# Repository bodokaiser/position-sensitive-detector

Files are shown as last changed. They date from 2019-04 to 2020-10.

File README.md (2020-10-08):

# Position-sensitive detector

Position-sensitive detector using the Hamamatsu S5991-01 position-sensitive photodiode.

| Parameter | Value |
| --------- | ----- |
| Spatial resolution | 2 um |
| Bandwidth | 1400 kHz |
| Input voltage | +- 15 V |
| Output voltage | +- 12 V |

detector

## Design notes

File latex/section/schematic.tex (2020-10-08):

\section{Schematic}

The present section discusses the critical sections of the electrical schematics and should be consulted for reference if parameters, for example, bandwidth or gain, need to be adjusted.

\subsection{Photodiode frontend}

The photodiode frontend is responsible for converting the photocurrent to a voltage.
The most simple frontend, a resistor, has limited bandwidth.
Using a transimpedance amplifier, we can decouple the output voltage from the voltage swing across the diode.
The bandwidth is now limited by the amplifier gain.

\begin{figure}[H]
	\centering
	\includestandalone[mode=buildnew]{figure/circuit/amplifier-transimpedance-input-capacitance}
 	\caption{Transimpedance amplifier for photodiode}\label{fig:transimpedance_amplifier}
\end{figure}

\Cref{fig:transimpedance_amplifier} shows a transimpedance amplifier frontend circuit representing the photodiode by a current source with capacitance.
The current source relates to the power of the incident light by
\begin{equation}
I_\text{in} = S(\lambda) P,
\end{equation}
wherein $S(\lambda)$ is the spectral responsivity, also known as photosensitivity, and $P$ is the power of the light beam.

A class 2 laser can be operated without safety googles.
For a Class 2 laser, the beam power is limited to $P\leq\SI{1}{\milli\watt}$. With $S=\SI{0.6}{\ampere\per\watt}$, the photocurrent is limited to $I_\text{in}\leq\SI{0.6}{\milli\ampere}$.

The operational amplifier's output voltage in the transimpedance configuration is equal to
\begin{equation}
	V_\text{out} = - R_f I_\text{in}.
	\label{eq:transimpedance_amplifier_output_voltage}
\end{equation}
The operational amplifier's output voltage is determined by it's supply voltages.
For a rail-to-rail operational amplifier it is equal to the supply voltage.
For example, if the supply voltage is \SI{\pm5}{\volt}, \cref{eq:transimpedance_amplifier_output_voltage} gives us a value for the feedback resistance,
\begin{equation}
	R_f\geq\abs{\frac{V_\text{out}}{I_\text{in}}}=\abs{\frac{V_\text{supply}}{I_\text{in}}}
	\label{eq:feedback_resistance}.
\end{equation}
Using the previous estimated photocurrent of a class 2 laser, $I_\text{in}=\SI{0.6}{\milli\ampere}$, $V_\text{supply}=\SI{\pm5}{\volt}$, and \cref{eq:feedback_resistance}, we find that $R_f\approx\SI{9}{\kilo\ohm}$ would make our transimpedance amplifier saturate at the maximal expected light power.

A feedback capacitance
\begin{equation}
	C_f\geq\sqrt{\frac{C_\text{in}}{2\pi R_f f_u}},
	\label{eq:feedback_capacitance}
\end{equation}
wherein $f_u$ is the \gls{gbp} of the operational amplifier,
 is sufficient for stability.
 In general, the input capacitance of the operational amplifier adds to the input capacitance.
 In practice, solder joints and \gls{pcb} traces may add to the capacitance such that a slightly higher value than given by \cref{eq:feedback_capacitance} is recommended.
 However, if the feedback capacitance is too high, we remove high-frequency components of our signal, which might be of interest.
 
The photodiode's datasheet specifies the capacitance $C_\text{in}$ to be about \SI{90}{\pico\farad} if reverse-biased at \SI{10}{\volt}.
The differential- and common-mode input capacitance of the OPA847 operational amplifier add up to a total input capacitance of \SI{98}{\pico\farad}.
Using $R_f=\SI{10}{\kilo\ohm}$ and \gls{gbp} of $f_u=\SI{10}{\mega\hertz}$, a feedback capacitance of at least $C_f=\SI{12.5}{\pico\farad}$ should be choosen.

\subsection{Voltage regulator}

We use two voltage regulators to maintain a constant voltage of \SI{\pm12}{\volt} from the external \SI{\pm15}{\volt} power supply. The \SI{\pm12}{\volt} voltage powers most components except the transimpedance amplifiers of the detector.
Using a dedicated pair of voltage regulators to power the transimpedance amplifiers decreases the load on the primary voltage regulator.

\Cref{fig:voltage_regulator} shows the circuitry of the primary voltage regulators that output \SI{\pm12}{\volt}.
The positive voltage regulator U1 of type LM317 and the negative voltage regulator U2 of type LM337 have an internal reference voltage of \SI{1.25}{\volt}.

\begin{figure}[H]
	\centering
	\includestandalone[mode=buildnew]{figure/circuit/voltage-regulator}
	\caption{Dual supply voltage regulator}\label{fig:voltage_regulator}
\end{figure}

The voltage divider comprising R1 and R2 fixes the output voltage according to
\begin{equation}
	V_\text{out}=\SI{1.25}{\volt}\left(1+\frac{R_2}{R_1}\right).
\end{equation}
With $R1 = \SI{240}{\ohm}$ and $R2 = \SI{2.2}{\kilo\ohm}$, the output voltage is about \SI{12.7}{\volt}, which leaves enough space for potential voltage drops in, for example, the operational amplifiers.

Diodes D1 and D3 ensure that the capacitors C3 and C5 can discharge over the external power supply.

The application notes of one of the voltage regulator's datasheets describe the presented design.
That is also the reason for not using fixed voltage regulators in this case.

\subsection{Voltage reference}

Reverse biasing the photodiode decreases it's capacitance and thereby increases the bandwidth.
The reverse bias voltage needs to be well controlled not to cause any side-effects.
Therefore, we utilize a voltage reference to supply a highly-regulated reverse voltage for the photodiode.

\begin{figure}[H]
	\centering
	\includestandalone[mode=buildnew]{figure/circuit/voltage-reference}
	\caption{Voltage reference to reverse bias the photodiode}\label{fig:voltage_reference}
\end{figure}

\Cref{fig:voltage_reference} shows the schematic of the reverse-bias voltage reference.
The capacitors C1 and C3 intercept voltage fluctuations. 
Resistor R1 forms a low-pass with capacitor C2 that suppresses frequencies above 160 Hz.

\subsection{Analog arithmetic}

Finally, we need to add and subtract the four different voltage signals of the position-sensitive photodiode to obtain quantities proportional to the incident light beam's center-of-mass.
We achieve immutability of the input signals for addition and subtraction with the summing amplifier.
We extend the summing amplifier to allow negative signs, i.e., subtraction.

\begin{figure}[H]
	\centering
	\includestandalone[mode=buildnew]{figure/circuit/amplifier-arithmetic}
	\caption{Summing and difference amplifier}\label{fig:amplifier_arithmetic}
\end{figure}

\Cref{fig:amplifier_arithmetic} shows such an arithmetic amplifier.
According to \cite[p. 5]{Tietze15} the output voltage is given by
\begin{equation}
	V_\text{out}=-\frac{R_1}{R_f}V_1-\frac{R_2}{R_f}V_2+\frac{R_3}{R_f}V_3+\frac{R_4}{R_f}V_4.
	\label{eq:arithmetic_amplifier_output_voltage}
\end{equation}

It is an excellent directive to have a well-controlled bandwidth.
On this account, we include capacitor $C_f$ to control the frequency response of the amplifier. 
For the resistor and capacitor configuration used in \cref{fig:amplifier_arithmetic}, the bandwidth is equal to
\begin{equation}
	\frac{1}{2\pi R_fC_f}\approx\SI{3}{\mega\hertz},
\end{equation}
magnitudes more than the bandwidth of our transimpedance amplifiers.
We place an additional capacitor with feedback capacitance at the non-inverting input of the operational amplifier to obtain a symmetric frequency response for the positive terms in \cref{eq:arithmetic_amplifier_output_voltage}.

The value of the resistors is \SI{10}{\kilo\ohm} to limit the current flow.

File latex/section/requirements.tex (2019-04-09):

\section{Requirements}

% TODO: precision and accuracy
% TODO: motivate bandwidth 1 kHz

The device should be powered by a dual voltage supply of \SI{15}{\volt} using a 4 pin LEMO connector.
The components on the printed circuit board should be assembled using surface-mount technology.
The device including casing should have a width below \SI{8}{\centi\meter} and a height below \SI{20}{\centi\meter}, preferably smaller, such that it can be integrated easily into existing optical setups.
The optical detector should be located as close to the bottom of the device as possible, as it allows greater height compatibility.

The spatial resolution of the center of mass of the incident light should be about \SI{1}{\micro\meter}.
Offset errors are tolerable as long as precision is high.
We aim for a signal bandwidth of \SI{10}{\kilo\hertz}.
The radiant flux of the incident light should be in the microwatt range.

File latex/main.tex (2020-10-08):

\documentclass[
	a4paper,
	parskip
]{scrartcl}

\usepackage[english]{babel}
\usepackage{authblk}
\usepackage{amsthm}
\usepackage{amsmath}
\usepackage{amssymb}
\usepackage{booktabs}
\usepackage{float}
\usepackage{multirow}
\usepackage{enumitem}
\usepackage{physics}
\usepackage{siunitx}
\usepackage{hyperref}
\usepackage{cleveref}
\usepackage{subcaption}
\usepackage{pgfplots}
\usepackage[backend=bibtex]{biblatex}
\usepackage{csquotes}
\usepackage[american]{circuitikz}
\usepackage{glossaries}
\usepackage[subpreambles=true]{standalone}

\makeglossaries
\newglossaryentry{s5990}{name=S5990, description={Hamamatsu two-dimensional PSD}}
\newacronym{ic}{IC}{integrated circuit}
\newacronym{ir}{IR}{infrared}
\newacronym{psd}{PSD}{position-sensitive detector}
\newacronym{gbp}{GBP}{gain-bandwidth-product}
\newacronym{pcb}{PCB}{printed circuit board}
\newacronym{bom}{BOM}{bill of materials}
\newacronym{smd}{SMD}{surface mounted device}
\newacronym{sma}{SMA}{SubMiniature version A}
\newacronym{bnc}{BNC}{Bayonet Neill–Concelman}
\newacronym{html}{HTML}{hypertext markup language}

\pgfplotsset{compat=1.17}

\graphicspath{{image/}}

\bibliography{literature.bib}

% https://tex.stackexchange.com/questions/247681/how-to-create-checkbox-todo-list/313337
\newlist{todolist}{itemize}{2}
\setlist[todolist]{label=$\square$}

\title{Position-sensitive detector}
\author{Bodo Kaiser}
\affil{Ludwig-Maximilians-Universität München}
\affil{\textit{bodo.kaiser@physik.uni-muenchen.de}}

\begin{document}

\maketitle
\tableofcontents

\include{section/introduction}
\include{section/position-sensitive-photodiode}
\include{section/operational-amplifier}
\include{section/schematic}
\include{section/production}
\include{section/measurement}

\appendix
\include{appendix/troubleshooting}

\printglossaries
\printbibliography

\end{document}

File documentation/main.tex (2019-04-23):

\documentclass[
	a4paper,
	parskip
]{scrartcl}

\usepackage[english]{babel}
\usepackage{authblk}
\usepackage{amsthm}
\usepackage{amsmath}
\usepackage{amssymb}
\usepackage{booktabs}
\usepackage{float}
\usepackage{multirow}
\usepackage{physics}
\usepackage{siunitx}
\usepackage{hyperref}
\usepackage{cleveref}
\usepackage{subcaption}
\usepackage{pgfplots}
\usepackage[
  backend=biber,
  sorting=none
]{biblatex}
\usepackage[american]{circuitikz}
\usepackage{glossaries}

\addbibresource{literature.bib}

\makeglossaries
\newglossaryentry{s5990}{name=S5990, description={Hamamatsu two-dimensional PSD}}
\newacronym{psd}{PSD}{position-sensitive detector}
\newacronym{gbp}{GBP}{gain-bandwidth-product}

\title{Position-sensitive device}
\author{Bodo Kaiser}
\affil{Ludwig-Maximilians-Universität München}
\affil{\textit{bodo.kaiser@physik.uni-muenchen.de}}

\begin{document}

\maketitle
\tableofcontents

\include{section/introduction}
\include{section/requirements}
\include{section/detector}
\include{section/preamplifier}
\include{section/power}

% TODO: signal processing of non-linear response Cui10
% TODO: mention current analog-to-digital-converter in a digital signal processing section

% TODO: bill of materials / component and package selection section
% TODO: pcb design section
% TODO: manufacturing section
% TODO: section for electrical and optical test setups to check functionality

\printglossaries
\printbibliography

\end{document}

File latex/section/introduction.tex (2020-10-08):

\section{Introduction}

We define a position-sensitive device as a device that outputs voltages proportional to the center of mass coordinates of a light beam incident on a sensitive area.

The present document summarizes the insights acquired on the journey of building such a device.

\subsection{Motivation}

Position-sensitive devices are used in a wide range of industrial and commercial applications, including displacement sensing and beam alignment, see Ref.~\cite[p.~22]{Maekynen00}.

We are interested in using a position-sensitive device for beam pointing alignment in our quantum optics laboratory.

The beam pointing refers to a laser beam's spatial focus and can change through thermal and mechanical effects.
Uncompensated changes in beam alignment can quickly degrade the overall performance of an optical system.
Therefore, it is crucial to align the beam pointing to ensure the optical system's proper operation at hand.

\subsection{Overview}

This document is organized as follows.

The first two sections introduce the theory of the (position-sensitive) photodiode and the operational amplifier.
These sections are rather elaborate and should be skipped by the pragmatic scientist.

The third section describes the (electrical) schematics of the detector.
If you want to adjust parameters, e.g., gain or bandwidth, you should read these sections.

The fourth section is the only significant section if you want to build a \gls{psd}.
If you also want an example of using the \gls{psd} in an optical setup to determine the spatial resolution, you should also read the fifth section.
Finally, the appendix gives some guidance on troubleshooting.

\subsection{Requirements}

The requirements are specified rather loose. The only hard requirement concerns the connectors and voltages of the power supply. The power connector should be a LEMO4 whose pin configuration is compatible with the \SI{\pm15}{\volt} dual-voltage power supplies used in the labs. Features that would be nice to have are:
\begin{enumerate}
	\item The device should be sensible with optical powers that are safe to operate, i.e., $P<\SI{1}{\micro\watt}$. There is no preferred wavelength.
	\item For easy integration into existing optical setups, the device should be as compact as possible. Additional space, if needed, should be occupied by elonging the height. The sensitive area of the detector should be on the bottom. The connectors should be on the top to avoid cables blocking the beam path.
	\item It should be possible to mount different detector sizes on the device.
\end{enumerate}
The range of the output voltages of the device can be chosen for the optimal signal-to-noise ratio.

\subsection{Specification}

\begin{figure}[H]
	\centering
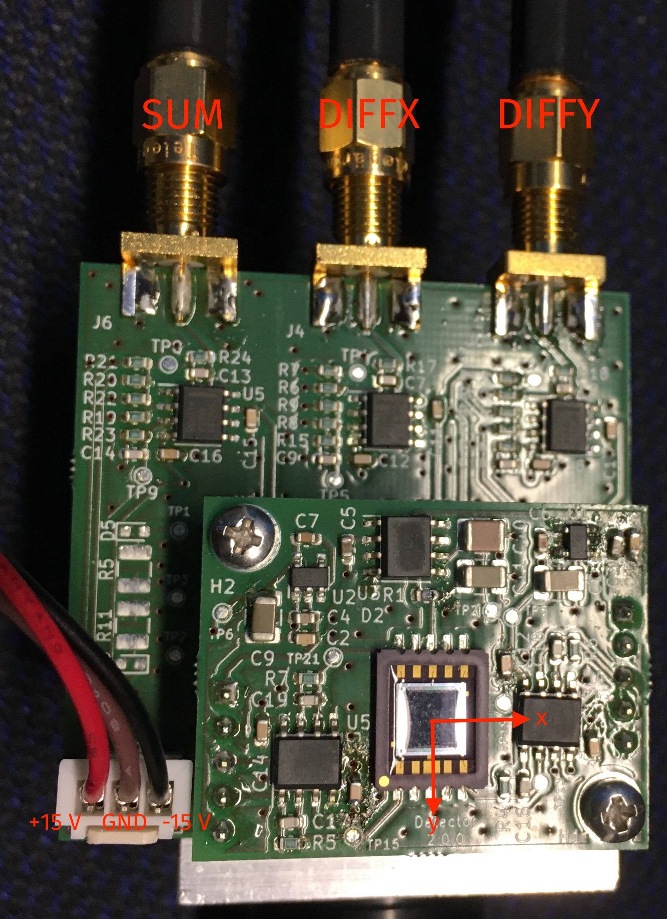
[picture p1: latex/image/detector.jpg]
	
	\caption{\gls{psd} on optical mount with connected cables}\label{fig:detector}
\end{figure}
\Cref{fig:detector} shows an image of the \gls{psd}.
The output voltage signals can be tapped from the upper \gls{sma} connectors.
The upper left connector gives the SUM voltage which reflects the total intensity of the optical signal.
The upper center connector gives the DIFFX voltage which reflects the difference proportional to the horizontal position on the sensitive area.
The upper right connector gives the DIFFY voltage which is proportional to the vertical position.
The SUM voltage is required to normalize the difference signals.
The DIFFX voltage increases when moving the light beam on the sensitive area to the right while the DIFFY voltage increases while moving the light beam to the bottom.
The device is powered by a 3-pin connector.
The outer (left) cable is the positive \SI{+15}{\volt} supply while the opposite cable is negative \SI{-15}{\volt} supply.
The center cable of the 3-pin connector has to reference ground.
The power connector has no polarity protection so be careful!

\begin{table}[htb]
  \centering
  \begin{tabular}{lcccc}
    \toprule
      Parameter & Minimum & Typical & Maximum \\
    \midrule
      Output voltages & \SI{-13}{\volt} & \SIrange{-2}{+2}{\volt} & \SI{+13}{\volt} \\
      Supply voltages & \SI{\pm13}{\volt} & \SI{\pm15}{\volt} & \SI{\pm37}{\volt} \\
      Spatial resolution & \SI{5.0}{\micro\meter} & \SI{2}{\micro\meter} & \SI{1}{\micro\meter} \\
      Bandwidth & & \SI{1400}{\kilo\hertz} & \\
    \bottomrule
  \end{tabular}
  \captionsetup{width=.8\textwidth}
  \caption{Specifications of the presented \gls{psd}}\label{tab:specifications}
\end{table}
\Cref{tab:specifications} summarizes the specifications of the presented \gls{psd}.
These specifications are only a rough estimate and we only assembled one \gls{psd} so far.

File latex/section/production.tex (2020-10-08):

\section{Production}

The production of the position-sensitive device involves the necessary steps to produce the detector and arithmetic \gls{pcb}.

It's best to first do the arithmetic board and if it works, proceed with the detector.
Of course, if you only need one of the boards, perform the following steps only once.

\subsection{Commissioning}

% TODO: screenshots of HTML BOM files

Before we can assemble the \gls{pcb}s, we need to gather the required components and order missing pieces.

The list of the required components is usually known as the \gls{bom}.
You can generate a current \gls{bom} directly from \href{https://kicad-pcb.org}{KiCad} by using the \href{https://github.com/openscopeproject/InteractiveHtmlBom}{InteractiveHtmlBom} plugin.
The plugin generates an \gls{html} file that lists the components and their respective placement on the \gls{pcb}.
\Cref{fig:kicad_interactive_html_bom_plugin_menu} shows where to find the plugin in the \gls{pcb} editor menu.
You can check if the parts are stocked and placed.
\begin{figure}[H]
	\centering
	
	\caption{Menu entry for the \href{https://github.com/openscopeproject/InteractiveHtmlBom}{InteraciveHtmlBom} plugin for \href{https://kicad-pcb.org}{KiCad}}\label{fig:kicad_interactive_html_bom_plugin_menu}
\end{figure}
\Cref{fig:kicad_interactive_html_bom_plugin_arithmetic} and \cref{fig:kicad_interactive_html_bom_plugin_detector} show the view of the generated \gls{html} for the arithmetic and detector board.
\begin{figure}[H]
	\centering
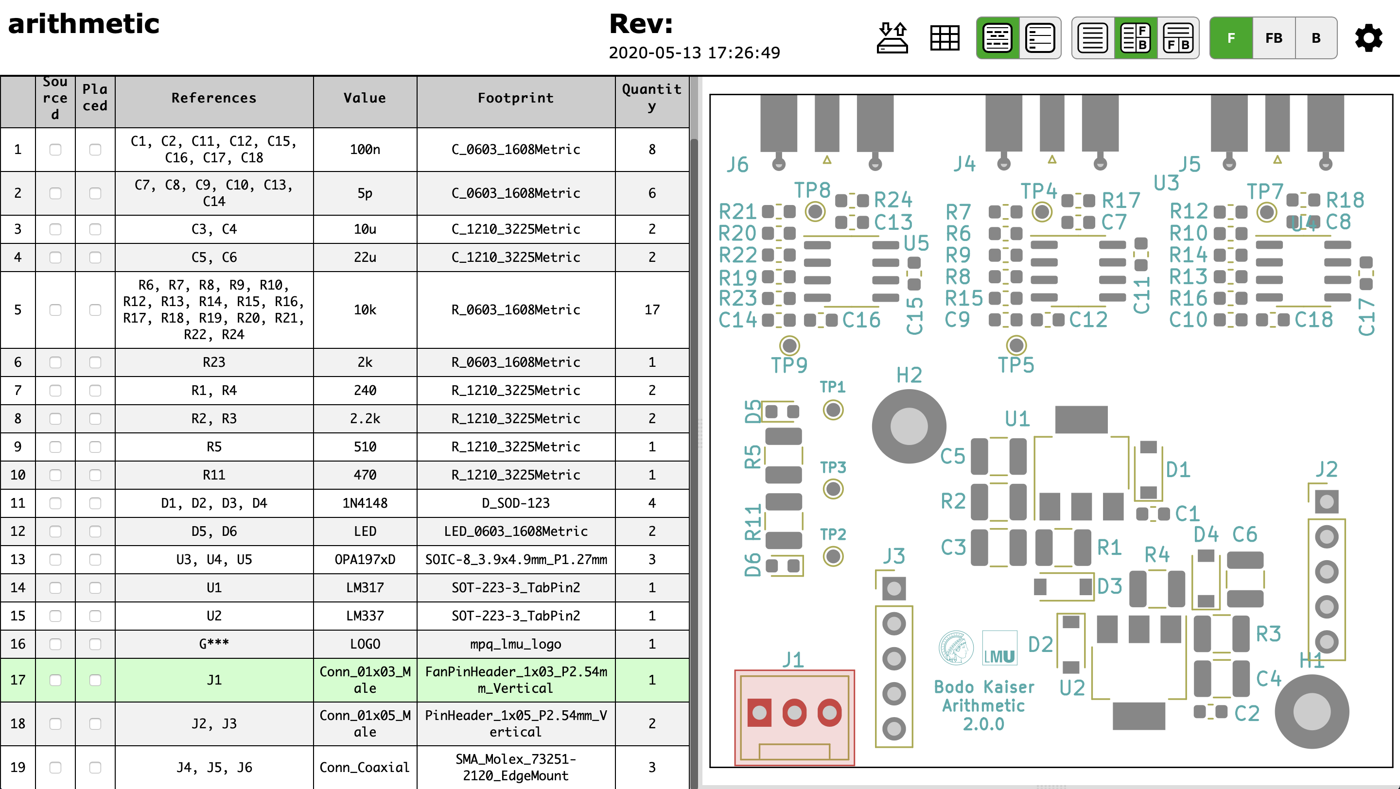
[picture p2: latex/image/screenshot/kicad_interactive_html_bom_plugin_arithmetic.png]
	
	\caption{Arithmetic board view of the \href{https://github.com/openscopeproject/InteractiveHtmlBom}{InteraciveHtmlBom} plugin}\label{fig:kicad_interactive_html_bom_plugin_arithmetic}
\end{figure}
\begin{figure}[H]
	\centering
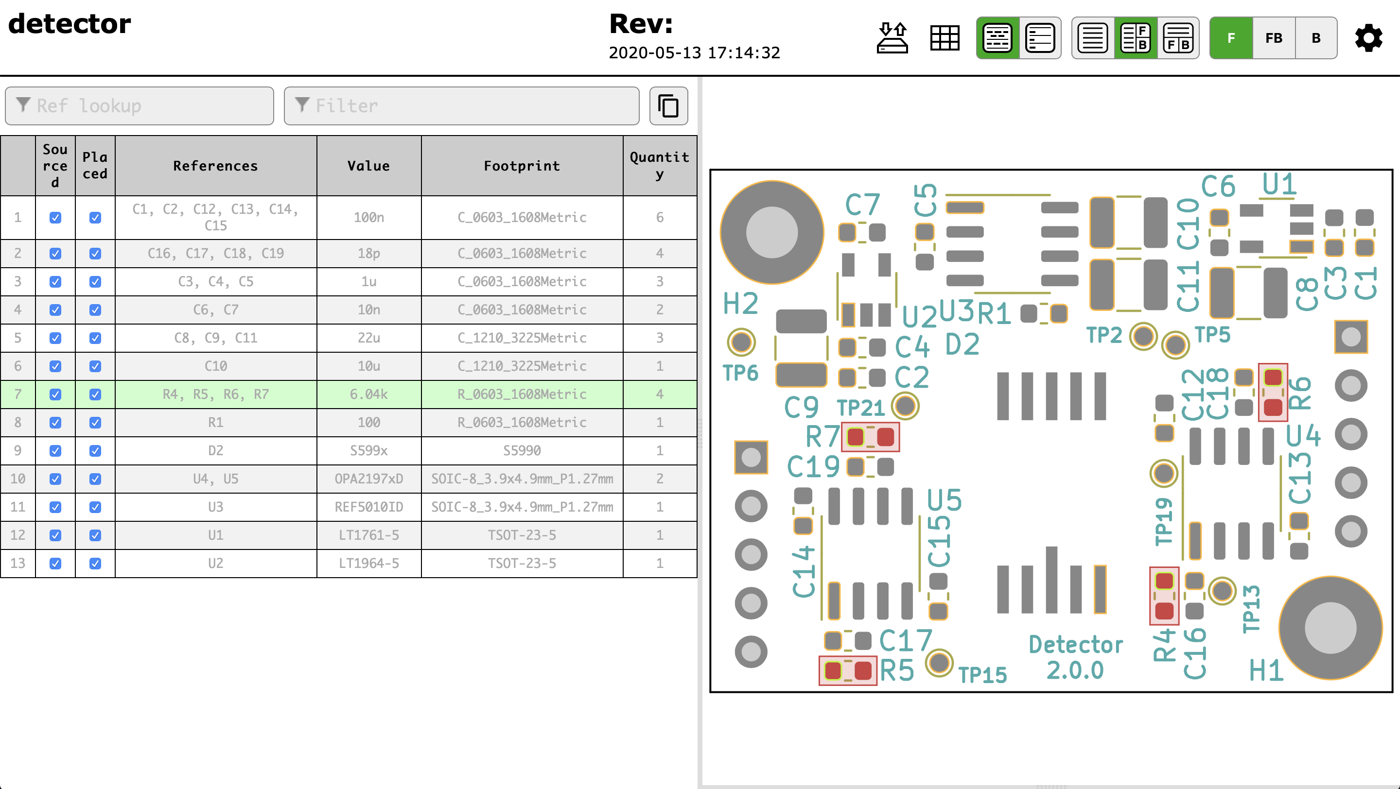
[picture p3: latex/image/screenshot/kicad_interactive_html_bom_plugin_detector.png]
	
	\caption{Detector board view of the \href{https://github.com/openscopeproject/InteractiveHtmlBom}{InteraciveHtmlBom} plugin}\label{fig:kicad_interactive_html_bom_plugin_detector}
\end{figure}
Start by checking the local inventory for the components listed by the generated \gls{html} \gls{bom}.
If certain elements are missing, you can check the \path{BOM.xlsx} file inside the project repository.
It contains part numbers and product links from major electronic distributors.
If you order, double-check with the generated \gls{html} \gls{bom}.
There might be errors, e.g., wrong casing sizes in the \path{BOM.xlsx} as it is potentially outdated.

\subsection{Manufacturing}

In the manufacturing process, we solder the components onto the PCB.
We recommend to proceed in the following steps:

\begin{enumerate}
    \item Put on rubber gloves as the solder paste is potentially hazardous.
    \item  Take out the solder paste from the fridge and let it reach room temperature\footnote{It is possible to use the cold solder paste directly, but it makes the handling more difficult as the paste is less fluid.}.
    \item Place the solder paste onto the contacts of the \gls{pcb}\footnote{Generally speaking, it is better to have too much solder paste then too less. If there is a small overlap between the contacts, this is fine as the solder will shrink when transitioning to a liquid phase in the oven.}.
    \item Place the \gls{smd} components onto the solder with a tweezer\footnote{Start with the larger components and then progress to the smaller ones}.
    \item Start the oven and adjust the frame on which you place the board with the screw to the appropriate size. Use an empty \gls{pcb} for this.
    \item Select the profile SMD180 and follow the instructions of the oven.
    \item Inspect the board for misplaced components and unmelted solder, and fix them by hand soldering\footnote{You can use the solder heat gun to melt the remaining solder paste or remove misplaced components. 
However, you might blow away small capacitors.}.
	\item Perform electrical testing as described in the next section.
	\item Solder remaining components, for example, the \gls{sma} mounts or the pin headers, by hand.
\end{enumerate}

\subsection{Electrical testing}

With the electrical testing, we want to confirm that the solder connections and components work as expected.
The most basic check is that the supply voltages are correct.
More elaborated checks concern the operational amplifiers but are out of the scope of this document.

For the arithmetic perform the following checks in the given order.
Skipping steps might lead to permanent damage!
\begin{todolist}
	\item Leave the arithmetic board unpowered and check for high resistance between the supply lines through the test points TP1 (\SI{+12}{\volt}), TP2 (GND), and TP3 (\SI{-12}{\volt})\footnote{If there is low resistance ($>\SI{10}{\kilo\ohm}$), you probably have a short through soldering.}.
	\item Configure the power supply to provide a dual voltage of \SI{\pm15}{\volt}\footnote{Alternatively, use two single voltage sources set to \SI{15}{\volt} and connect the negative port of one of the voltage sources with the other one's positive voltage.}. If possible, limit the current of the voltage sources.
	\item Confirm that the output voltages are correct with the multimeter.
	\item Connect the power supply with the arithmetic board but double-check the polarity.
	\item The voltage between TP2 and TP1 should read around \SI{+12}{\volt} while the voltage between TP2 and TP3 should read about \SI{-12}{\volt}.
	\item Confirm that the supply voltages reach the op-amps.
	\item Check the temperature of the \gls{ic}s. If any \gls{ic} is very hot, there is a short.
	\item Check if the op-amps' output voltage changes by grounding the inverting input.
\end{todolist}

For the detector perform the following checks in the given order.
Skipping steps might lead to permanent damage!
\begin{todolist}
	\item Leave the detector board unplugged and confirm high resistance between GND (you can use the middle pin of the headers), TP5 (\SI{+5}{\volt}), and TP6 (\SI{-5}{\volt}).
	\item Confirm a change of the voltage between the photodiode and GND's outer pins while illuminating the sensitive area of the photodiode with a laser pointer.
	\item Mount the detector board on the arithmetic board, and measure the detector board's supply voltages.
	\item Confirm that the voltage reference (U3) outputs \SI{10}{\volt} and that the op-amps have the correct supply voltage of \SI{\pm5}{\volt}.
\end{todolist}

Finally, we test the arithmetic amplifiers on the arithmetic board.
\begin{todolist}
	\item Mount the detector onto the arithmetic board.
	\item Measure the voltage at the outputs of the operational amplifiers of the arithmetic board. For the summing amplifier (U5), we expect an increase in voltage when illuminating the photodiode with the laser pointer.
For the difference amplifiers (U3, U4), we expect the voltage to change when moving the laser pointer's focal spot on the photodiode.
\end{todolist}

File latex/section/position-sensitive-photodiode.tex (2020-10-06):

\section{Position-sensitive photodiode}

The present section gives an introduction to the semiconductor theory for a position-sensitive photodiode.
We start from the description of a p-n junction and extend the description to the position-sensitive photodiode.
After that, we discuss the evolution of position-sensitive photodiode designs.
Finally, we derive an analytical relation between the photocurrents and the light focus's position on the sensitive area.

\subsection{Transverse photodiodes}

The purpose of the following section is to recall the mechanics of the (transverse) photoeffect observed in an illuminated p-n junction.
Figures and the description thereof are primarily based on Ref.~\cite{Simon13}.
A subtle difference in the depicted figures and the figures of Ref.~\cite{Simon13} is that we exchanged the order of p- and n-type semiconductors.
We found this order to be more intuitive when referring to a p-n junction.
\begin{figure}[H]
	\centering
	\includestandalone[mode=buildnew]{figure/diagram/pn-junction-separated}
	\caption{Separated p- and n-type semiconductor with holes (white) and electrons (black).}\label{fig:pn_junction_separated}
\end{figure}
\Cref{fig:pn_junction_separated} shows a separated p- and n-type semiconductor.
We see an illustration of the p- and n-type semiconductors with their respective mobile charge carriers in the upper half.
The p-type semiconductor has an excess of positive charge carriers (holes), depicted as white circles.
The n-type semiconductor has an excess of negative charge carriers (electrons), depicted as black circles.
The excess charge carriers form due to the implantation of acceptor and donator ions and are indicated as circles with plus and minus sign in \Cref{fig:pn_junction_separated}.
The implanted ions have more or fewer electrons than the atoms of the semiconductor material.
Therefore donating an electron or accepting an electron and effectively forming a hole as an absence of negative charge.
The lower half of \Cref{fig:pn_junction_separated} shows the energy band structure of both p- and n-type semiconductors.
The lower energy band represents the valence band made up of the tightly bound electrons.
The upper energy band represents the conduction band made up of electrons that are are not bound to a single atomic core but shared across the lattice.
Charge carriers in the conduction band can move freely and thereby contribute to the conductivity of the material.
For an undoped (intrinsic) semiconductor, the chemical potential is in the center of the bandgap between the conduction and valence band.
Doping shifts the chemical potential in the p- and n-type semiconductors.
In the p-type semiconductor, acceptor ions can take up electrons from the conduction band, thereby decreasing the chemical potential.
In the n-type semiconductor, donator ions contribute electrons to the conduction band, increasing the chemical potential.
\begin{figure}[H]
	\centering
	\includestandalone[mode=buildnew]{figure/diagram/pn-junction-combined}
	\caption{Combined p- and n-type semiconductor with holes (white) and electrons (black).}\label{fig:pn_junction_combined}
\end{figure}
In \Cref{fig:pn_junction_combined} the p- and n-type semiconductors are brought into contact with each other, forming a p-n junction.
Close to the junction, holes and electrons recombine due to a diffusion process, leaving an electrically charged area.
The electrically charged area creates an electrostatic potential across the junction, as illustrated in the lower part of \Cref{fig:pn_junction_combined}.
We refer to this area as the depletion region.
In \Cref{fig:pn_junction_combined} the depletion region expands between the dashed lines around the junction.
\begin{figure}[H]
	\centering
	\includestandalone[mode=buildnew]{figure/diagram/pn-junction-energy}
	\caption{Energy bands of the p-n junction.}\label{fig:pn_junction}
\end{figure}
The energy band diagram in \Cref{fig:pn_junction} accounts for the shift in energy due to the electrostatic potential.
The chemical potentials of both sides of the junction are now aligned.
The energy required to excite an electron on the p-type side from the valence to the conduction band and the energy needed to excite a hole from the conduction to the valence band are equal to the bandgap of the semiconductor.
Suppose one applies a reverse bias voltage across the p-n junction. In that case, the effective energy gap between conduction and valence band is reduced, the electrostatic potential increases, and the depletion region broadens.
\Cref{fig:pn_junction_reverse} depicts the situation of an applied reverse voltage.
\begin{figure}[H]
	\centering
	\includestandalone[mode=buildnew]{figure/diagram/pn-junction-energy-reverse}
	\caption{Energy band diagram of a reverse biased p-n junction.}\label{fig:pn_junction_reverse}
\end{figure}
The current-voltage characteristic of the p-n junction is described by the Schockley diode equation,
\begin{equation}
	I_\text{diode}=I_\text{sat}(T)\left(e^{eV/k_BT}-1\right)
	\label{eq:diode_current},
\end{equation}
wherein $I_\text{sat}\propto e^{-E_\text{gap}/k_BT}$ is the temperature dependent reverse bias saturation current and $V$ the voltage applied to the p-n junction.
Using the proportionality of the reverse bias saturation current, we can write,
\begin{equation}
	I_\text{diode}\propto e^{\left(eV-E_\text{gap}\right)/k_BT}-e^{-E_\text{gap}/k_BT}\label{eq:diode_current_prop},
\end{equation} 
which discloses the two effects contributing to the diode current.
The left-hand side of the proportionality of \Cref{eq:diode_current_prop} represents the current contribution due to intra-band excitation of charge carriers, whereas the right-hand side represents the current contribution due to inter-band excitation.
\begin{figure}[H]
	\centering
	\includestandalone[mode=buildnew]{figure/plot/diode-current-voltage}
	\caption{Current-voltage characteristics of a p-n junction with different levels of illumination.}\label{fig:pn_junction_iv}
\end{figure}
In \Cref{fig:pn_junction_iv} we see the current-voltage characteristics of the p-n junction under different levels of illumination.
For negative voltages, the p-n junction is operated under reverse bias.
If the reverse bias voltage exceeds the breakdown voltage, the p-n junction starts to conduct.
The reverse saturation current is the amount of current necessary for the breakdown. The curve shifts downwards with increasing illumination.
The separation between the non-illuminated (top curve) and illuminated curves represent the respective photocurrent.

The conversion rate of photons to photoelectrons depends on the type of the bandgap, i.e., direct or indirect, the wavelength $\lambda$ of the photon, and the temperature $T$.
Most photodiodes report a wavelength $\lambda$ dependent responsitivity $R$ which can be used to convert the radiant flux $P$ of the incident light to the generated photocurrent $I_\text{photo}$,
\begin{equation}
	I_\text{photo}=R(\lambda)P
	\label{eq:responsitivity}.
\end{equation}
For silicon-based p-n junctions, the responsitivity $R(\lambda)$ is between \SI{0.2}{\ampere\per\watt} at \SI{400}{\nano\meter} and \SI{0.6}{\ampere\per\watt} at \SI{950}{\nano\meter}.

\begin{figure}[H]
	\centering
	\includestandalone[mode=buildnew]{figure/diagram/pn-junction-energy-illumination}
	\caption{Energy diagram of a reverse biased p-n junction under illumination.}\label{fig:pn_junction_illumination}
\end{figure}
\Cref{fig:pn_junction_illumination} shows a p-n junction under reverse bias where a photon excites an electron-hole pair in the depletion region.
Due to the electrostatic potential, the electrons are accelerated to the right. Analogue, the holes are accelerated to the left. The photocurrent, a diode current, \Cref{eq:diode_current}, flows across the junction.

\subsection{Lateral photodiodes}

In the previous section, we discussed the transversal photoeffect associated with the p-n junction's illumination.
In addition to the transversal photoeffect, the lateral photoeffect was first discovered by W. Schottky~\cite{Schottky30} in 1930 and later rediscovered in 1957 by J. Wallmark~\cite{Wallmark57}.
In the present section, we summarize key results from Ref.~\cite{Noorlag74}, and Ref.~\cite{Woltring75}. The focus of our summary is on the most common position-sensitive photodiode design, the tetralateral photodiode.
\begin{figure}[H]
	\centering
	\includestandalone[mode=buildnew]{figure/diagram/pn-junction-lateral-cross-section}
	\caption{Cross section of a lateral photodiode.}\label{fig:lateral_photodiode_cross_section}
\end{figure}
\Cref{fig:lateral_photodiode_cross_section} depicts the cross-section of a lateral photodiode with a p-type semiconductor as the top, an n-type semiconductor as the middle layer, and a resistive material as the bottom layer.
The photodiode's common cathode is an electric contact into the top layer.
One can ground or apply a positive voltage to the common cathode. If we apply a positive voltage, we say that the photodiode is reverse-biased.
In contrast to the transversal photodiode, the lateral photodiode has two anode contacts positioned at the opposite sites embedded into the resistive layer.
An almost linear relation between the photocurrent at each of the anode contacts and the incident light spot's center-of-mass exists.
Therefore the lateral photodiode can be used to measure the spatial coordinate of an incident light spot.

The dynamics of the lateral photodiode are guided by the Lucovsky~\cite{Lucovsky60} equation,
\begin{equation}
	\nabla^2V=\frac{\rho}{w}J_s\left(e^{eV/k_BT}-1\right)-\frac{\rho_d}{w}J_p\label{eq:lucovsky_exact},
\end{equation}
wherein $V$ is the diode voltage, $\rho$ is the resistance per unit length of the resistive layer, $J_s$ is the reverse-bias saturation current and $J_p$ is the photocurrent generated due photon induced electron-hole excitation.
\Cref{eq:lucovsky_exact} can be obtained by a combination of the current density continuity equation with Ohm's law and the Schottky equation, \Cref{eq:diode_current}.

According to Ref.~\cite{Woltring75}, operation of the lateral in fully reverse-bias has the following benefits:
\begin{enumerate}
	\item Reduced signal loss.
	\item Improved response speed and resolution.
	\item Improved linearity of the position.
	\item Reduced temperature dependence.
\end{enumerate}
In electronic engineering literature, e.g., Ref.~\cite[p.~258]{Jung05}, one is sometimes discouraged from operating a photodiode under reverse-bias for the highest sensitivity as the reverse-bias increased the diode leakage (dark) current.
We believe that as long as the dark current is significantly smaller than the typical photocurrent, the photodiode should always be operated in the reverse-bias mode as recommended by Ref.~\cite{Noorlag74,Woltring75,Wang89,Hobbs11}.

Assuming a fully reverse-biased lateral photodiode, we have $eV/k_BT\ll1$ and \Cref{eq:lucovsky_exact} simplifies to a linear second order differential (Poisson) equation,
\begin{equation}
	\nabla^2V\approx-\frac{\rho}{w}\left(J_s+J_p\right)
	\label{eq:lucovsky_reverse_bias},
\end{equation}
which can be solved using variable separation and a product Ansatz.
The solution of \Cref{eq:lucovsky_reverse_bias} depends on the imposed boundary conditions.
The Dirichlet boundary condition, $V=0$, should be used if an electrical contact terminates the semiconductor. Otherwise, the Neumann boundary condition, $\pdv{V}{n}=0$, should be assumed.
\begin{figure}[H]
	\centering
	\includestandalone[mode=buildnew]{figure/diagram/pn-junction-lateral-contacts}
	\caption{Contact configurations of a lateral photodiode.}\label{fig:lateral_photodiode_contacts}
\end{figure}
In \Cref{fig:lateral_photodiode_contacts} we present three different contact configurations.
The left contact configuration, used by Wallmark, comprises four small contacts, see Ref.~\cite{Wallmark57}.
Assuming that the contact size is small compared to the photodiode's surface, we need to use the von Neumann boundary condition.
The middle contact configuration receives great attention from Noorlag~\cite{Noorlag74}.
On two opposite sides of the photodiode, an electric contact terminates the boundary while the remaining sides are left empty.
For two-dimensional position detection, one can create two electric contacts at another layer.
Mathematically we can express this configuration as a combination of Neumann and Dirichlet boundary conditions.
For the tetralateral configuration, we need to apply the Dirichlet boundary conditions for all sides.
For a rectangular tetralateral photodiode of width $l$, the explicit boundary conditions are,
\begin{align}
	V(0, y)=V(l,y)=0, && V(x,0)=V(x,l)=0.
\end{align}
Together with the initial condition that a focused light spot hits the photodiode at $(x^*,y^*)$,
\begin{equation}
	V_p(x,y, t=0)=I_p\frac{\rho}{w}\delta(x-x^*)\delta(y-y^*)
	\label{eq:lucovsky_initial},
\end{equation}
the general solution of the Lucovsky equation, \Cref{eq:lucovsky_reverse_bias}, for the tetralateral configuration reads,
\begin{equation}
	V^*_p(x,y)=I_p\frac{\rho}{w}\sum_{n\in\mathbb{Z}}\sum_{m\in\mathbb{Z}}\frac{\sin(m\pi x/l)\sin(m\pi x^*/l)\sin(n\pi y/l)\sin(n\pi y^*/l)}{(m^2+n^2)\pi^2}
	\label{eq:lucovsky_solution}.
\end{equation}
The current that flows through the $x1$ contact is given by
\begin{equation}
	I_{x1}(x^*,y^*)=\frac{w}{\rho}\int_0^l\dd{y}\eval{\pdv{V}{x}}_{x=0},
\end{equation}
respective
\begin{equation}
	I_{x1}(x^*,y^*)=\frac{2}{\pi}I_p\sum_{n\in\mathbb{Z}}\frac{\sin[(2n-1)\pi y^*/l]}{2n-1}\frac{\sinh[\abs{2n-1}\pi(1-x^*/l)]}{\sinh(\abs{2n-1}\pi)}
	\label{eq:lucovsky_current}.
\end{equation}
The solution does not disclose the linear relationship between anode current $I_{x1}$ and the incident spot light coordinate $x^*$.
Ref.~\cite[Fig.~7]{Woltring75} renders the non-linear distortion close to the boundaries as described by \Cref{eq:lucovsky_current}.
In order to show analytically that there is an almost linear relationship between $I_{x1}$ and $x^*$, we fix $y^*=l/2$, numerically evaluate the dominant terms and Taylor expand the terms to linear order,
\begin{align}
	I_{x1}(x^*,l/2)
	&=\frac{2}{\pi}I_p\sum_{n\in\mathbb{Z}}\frac{(-1)^{n+1}}{2n-1}\frac{\sinh(\abs{2n-1}\pi(1-x^*/l))}{\sinh(\abs{2n-1}\pi)}\\
	&\approx I_p\left\{0.25-0.41731\left(\frac{x}{2l}-1\right)\right\}+\mathcal{O}\left(\left(\frac{x^*}{l}-\frac{1}{2}\right)^2\right).
\end{align}
Using the difference between two opposite contacts and normalizing for the total photocurrent, we find,
\begin{equation}
	\frac{I_{x2}(x^*,l/2)-I_{x1}(x^*,l/2)}{I_{x1}(x^*,l/2)+I_{x2}(x^*,l/2)}
	\propto\frac{x}{l},
\end{equation}
which indeed is linear in $x$.

According to Ref.~\cite[p.~41]{Noorlag74}, the tetralateral photodiode has benefits in manufacturing, although its linearity is below the dual lateral photodiode, still better than the Wallmark type, see Ref.~\cite{Woltring75}.
Recent contact configurations have improved upon the tetralateral design to improve the linearity.
For example, the commercially available pin-cushion tetralateral photodiode, discussed in Ref.~\cite{Doke87,Wang89}, shows good linearity over a large area.
The center-of-mass of an incident light spot at $(x^*,y^*)$ can be recovered from the anode currents via,
\begin{align}
	\frac{\left(I_{x2}+I_{y1}\right)-\left(I_{x1}+I_{y2}\right)}{I_{x1}+I_{x2}+I_{y1}+I_{y2}}=\frac{2x^*}{l} &&
	\frac{\left(I_{x2}+I_{y2}\right)-\left(I_{x1}+I_{y1}\right)}{I_{x1}+I_{x2}+I_{y1}+I_{y2}}=\frac{2y^*}{l}	.
\end{align}
The datasheet~\cite{HamamatsuS5990} of the \gls{s5990}, a pin-cushion tetralateral photodiode, discloses the position detectability of a light spot of size \SI{0.2}{\milli\meter} over a scan interval of \SI{0.4}{\milli\meter} which does not show any non-linear distortion.

\subsection{Equivalent circuit}

In the previous section, we described the physics behind the lateral photodiode.
In the current section, we want to ignore microscopic details and concentrate on real tetralateral photodiodes' electrical properties.

In \Cref{fig:tetralateral_photodiode_equivalent} the equivalent circuit of a tetralateral photodiode is depicted.
The tetralateral photodiode has four anode connections X1, X2, Y1, and Y2 which are connected to the junction via position-dependent resistances $R_1$, $R_2$, $R_3$, and $R_4$.
The actual junction is equivalent to two current sources $I_p,I_d$, a resistor $R_d$, and a capacitor $C_d$ in parallel.
The first current source $I_p$ represents the generated photocurrent with typical values between \si{\micro\ampere} and \si{\milli\ampere}.
The second current source $I_d$ represents the generated leakage or dark current with typical values between \si{\pico\ampere} and \si{\nano\ampere}.
\begin{figure}[H]
	\centering
	\includestandalone[mode=buildnew]{figure/circuit/photodiode-tetralateral}
	\caption{Equivalent circuit of a tetralateral photodiode.}\label{fig:tetralateral_photodiode_equivalent}
\end{figure}
The resistance $R_d$ is referred to as interelectrode resistance and is about \SI{10}{\kilo\ohm}.
The capacitance $C_d$ is also referred to as terminal capacitance and is about \SI{150}{\pico\farad}.
Resistance $R_d$ and capacitance $C_d$ form an RC pole which frequency is given by,
\begin{equation}
	f_d=\frac{1}{2\pi R_dC_d}.
\end{equation}
For $R_d=\SI{10}{\kilo\ohm}$ and $C_d=\SI{100}{\pico\farad}$ the cut-off frequency $f_d$ of the pole is about \SI{1}{\mega\hertz}, representing the intrinsic bandwidth limit of the detector.

\subsection{Signal-to-noise ratio}

% TODO: check out Radeka1974 and Narayanan1997 for more details
% TODO: estimate non-linear errors

According to \cite{Woltring75}, the thermal (Johnson) noise of the resistive component of the lateral photodiode is the dominant noise source.
The thermal noise is given by,
\begin{equation}
	I_t=\sqrt{\frac{4k_BTB}{R}},
\end{equation}
wherein $B$ denotes the bandwidth to consider.
At room temperature $T=\SI{300}{\kelvin}$ and an interelectrode resistance of $R_d=\SI{10}{\kilo\ohm}$, we find a noise current density due to thermal noise of $i_t=\SI{2}{\pico\ampere\per\sqrt\hertz}$.
If we estimate for the complete bandwidth supported by the detector, we find a root-mean-squared noise current of $I_t=\SI{2}{\nano\ampere}$.
A more realistic bandwidth incoporating later analog components would be $B=\SI{10}{\kilo\hertz}$, yielding $I_t=\SI{200}{\pico\ampere}$.

% TODO: noise propagation from detector to anodes
In any case, we cannot say for sure how these noise sources propagate into position detection noise.
For instance, if the noise propagates in the same proportions over the anodes, any error should cancel out when calculating the position.

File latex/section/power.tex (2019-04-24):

\section{Power management}

\subsection{Supply filter}

The purpose of the supply filter is to filter out noise from the power supply and buffer voltage peaks.
A simple embodiment of a supply filter is that of an RC low-pass filter as illustrated in \Cref{fig:filter_lowpass}.
\begin{figure}[H]
	\centering
	\begin{circuitikz}
		\draw (0, 0) node[ocirc, label=$V_\text{in}$]{} to[resistor, label=$R$] ++(4, 0) node(node)[circ]{};
		\draw (node) -- ++(2, 0) node[ocirc, label=$V_\text{out}$]{};
		\draw (node) to[capacitor, label=$C$] ++(0, -2) node[ground]{};
	\end{circuitikz}
	\caption{Passive low-pass filter using an RC circuit.}\label{fig:filter_lowpass}
\end{figure}
In \Cref{fig:filter_lowpass} the input voltage is connected through a resistor $R$ with the output voltage.
After the resistor $R$, a capacitor $C$ is connected with ground.
The transfer function of the RC low-pass filter can be obtained from the voltage divider with complex impedances,
\begin{equation}
	\frac{V_\text{out}}{V_\text{in}}
	=\frac{Z_C}{Z_R+Z_C}
	=\frac{1}{1+j\omega RC}.
	\label{eq:transfer_filter_rc}
\end{equation}
The absolute value of the transfer function,
\begin{equation}
	\abs{\frac{V_\text{out}}{V_\text{in}}}
	=\frac{1}{\sqrt{1+\left(f/f_{RC}\right)^2}},
\end{equation}
has a pole at frequency,
\begin{equation}
	f_{RC}=\frac{1}{2\pi RC}.
\end{equation}
% TODO: explain how to select R and C values for low-pass
The frequency response of an RC low-pass with pole frequency $f_{RC}=\SI{100}{\hertz}$ is visualized in \Cref{fig:bode_filter_rc}.
\begin{figure}[H]
	\centering
	\begin{tikzpicture}
		\begin{semilogxaxis}[xmin=1, xmax=1e6, xlabel=Frequency (Hz), ymin=-100, ymax=10, ylabel=Gain (dB), ytick={0, -20, -40, -60, -80}, grid=minor]
			\addplot[domain=1:1e9]{-10*log10(1+(x/100)^2)};
		\end{semilogxaxis}
	\end{tikzpicture}
	\caption{Bode plot of the frequency response of an RC low-pass at \SI{100}{\hertz}.}\label{fig:bode_filter_rc}
\end{figure}
We can see how the frequency response suppresses frequency above \SI{100}{\hertz}.
However, efficient frequency suppression starts at \SI{-80}{\decibel} which the given RC low-pass of \Cref{fig:bode_filter_rc} only satisfies for much higher frequencies than the pole frequency.

% TODO: give example of two pole filter and how to choose parameters
One approach to improve the frequency response of a filter is to introduce additional frequency poles.
In the limit of infinite many frequency poles, one is able to approach an ideal brick-wall filter.
The frequency response of an ideal brick-wall filter resembles a step function.
In practice, one finds good enough results for two pole filters.

% TODO: give example of capacitance multiplier and how to choose parameters
In addition to a multi-pole filter, a capacitance multiplier can be used to increase the effective capacitance of a filter.
The capacitance multiplier is described in Ref.~\cite[p.~536]{Hobbs11} and Ref.~\cite[p.~578]{Horowitz15}.

\subsection{Voltage regulator}

We use two voltage regulator to maintain a constant voltage of \SI{\pm12}{\volt} which is used to supply the operational amplifiers.

In general, one needs to decide between linear and switching voltage regulators.
Linear voltage regulators are less efficient than their switching counterparts but have better noise characteristics.
As efficiency is not a concern in our application, the better noise characteristics are a strong argument for the linear voltage regulators.
Linear voltage regulators require an input voltage greater than the output voltage.
The difference between input and output voltage is called the drop-out voltage.
The drop-out voltage is about \SIrange{2}{3}{\volt}

Linear voltage regulators are available with fixed and adjustable output voltage.
As we might need an additional voltage drop between the input voltage and the voltage regulator input, e.g. for input power filters, an adjustable voltage regulator would allow for more flexibility.
Moreover, we found the range of negative voltage regulators to be rather limited.

% TODO: working principle (how does R1, R2 on the adjustable terminal change the output voltage?)
\begin{figure}[H]
	\centering
	\begin{circuitikz}
		\draw (0, 0) node[vcc, rotate=90, label={[label distance=6]:\SI[retain-explicit-plus]{+15}{\volt}}]{} -- ++(1, 0) node(node1a)[circ]{} -- ++(4, 0) node(node1b)[circ]{} -- ++(0, 2) to[diode, l_=D1] ++(-4, 0) -- ++(0, -2);
		\draw (node1b) to[resistor, l_=R1, a^=\SI{120}{\ohm}] ++(0, -2) node(node2a)[circ]{} -- ++(-2, 0) -- ++(0, 2);
		\draw (node2a) -- ++(3, 0) node(node2b)[circ]{} to[diode, l=D3] ++(0, 2) node(node1c)[circ]{} -- ++(-3 ,0);
		\draw (node1c) -- ++(2, 0) node(node1d)[circ]{} to[ecapacitor, l_=C5, a^=\SI{1}{\micro\farad}] ++(0, -4) node(node3d)[circ]{} -- ++(-2, 0) node(node3c)[circ]{} -- ++(-3, 0) node(node3b)[circ]{} to[resistor, l^=R2, a_=\SI{980}{\ohm}] ++(0, 2);
		\draw (node2b) to[ecapacitor, l_=C3, a^=\SI{10}{\micro\farad}] (node3c);
		\draw (node1d) -- ++(1, 0) node[vcc, rotate=270, label={[label distance=6]:\SI[retain-explicit-plus]{+12}{\volt}}]{};
		\begin{scope}[xshift=3cm]
			\node[draw, rectangle, fill=white, minimum width=2cm, minimum height=1.2cm, label=U1]{};
			\node at (0, 0) {LM317};
		\end{scope}
		\draw (node3d) -- ++(1, 0) node[ground, rotate=90]{};
		\draw (node3b) -- ++(-5, 0) node[ground, rotate=270]{};
		\draw (node1a) to[ecapacitor, l_=C1, a^=\SI{100}{\nano\farad}] ++(0, -4) node(node3a)[circ]{};
		\draw (node3a) to[ecapacitor, l_=C2, a^=\SI{100}{\nano\farad}] ++(0, -4) node(node5a)[circ]{};
		\draw (node5a) -- ++(-1, 0) node[vee, rotate=270, label={[label distance=6]:\SI{-15}{\volt}}]{};
		\draw (node3b) to[resistor, l_=R3, a^=\SI{980}{\ohm}] ++(0, -2) node(node4b)[circ]{} to[resistor, l_=R4, a^=\SI{120}{\ohm}] ++(0, -2) node(node5b)[circ]{} -- (node5a);
		\draw (node3c) to[ecapacitor, l_=C4, a^=\SI{10}{\micro\farad}] ++(0, -2) node(node4c)[circ]{} to[diode, l_=D4] ++(0, -2) node(node5c)[circ]{} -- (node5b);
		\draw (node3d) to[ecapacitor, l_=C6, a^=\SI{1}{\micro\farad}] ++(0, -4) node(node5d)[circ]{} -- (node5c);
		\draw (node5d) -- ++(1, 0) node[vee, rotate=90, label={[label distance=6]:\SI{-12}{\volt}}]{};
		\draw (node5a) ++(2, 0) -- ++(0, 2) -- (node4b) -- (node4c);
		\begin{scope}[xshift=3cm, yshift=-8cm]
			\node[draw, rectangle, fill=white, minimum width=2cm, minimum height=1.2cm, label=below:U2]{};
			\node at (0, 0) {LM337};
		\end{scope}
		\draw (node5b) -- ++(0, -2) to[diode, l^=D2] ++(-4, 0) -- ++(0, 2);
	\end{circuitikz}
	\caption{Dual supply voltage regulator.}\label{fig:voltage_regulator_dual}
\end{figure}
\Cref{fig:voltage_regulator_dual} illustrates the schematic of the final dual voltage regulator supply circuit.
The input voltage is buffered by capacitors C1 and C2.
U1 and U2 denote the fixed positive and negative voltage regulators.
Resistors R1 and R2 configure the output voltage of U1 to about \SI[retain-explicit-plus]{+11.5}{\volt}.
Resistors R3 and R4 configure the output voltage of U2 to about \SI[retain-explicit-plus]{-11.5}{\volt}.
Capacitors C3, C4, C5 and C6 buffer the output voltage.
When the supply power is switched off and C3 or C5 discharges,
diodes D3 and D1 redirect the current back to the supply lines around the voltage regulators.

\subsection{Voltage reference}

A voltage reference is a high-precision linear (fixed) voltage regulator.
We use it as a voltage source for the sensible reverse bias voltage of the photodiode.
\begin{figure}[H]
	\centering
	\begin{circuitikz}
		\draw (0, 0) node[vcc, rotate=90, label={[label distance=6]:\SI{15}{\volt}}]{} -- ++(1, 0) node(node1a)[circ]{} to[capacitor, l_=C1, a^=\SI{1}{\micro\farad}] ++(0, -4) node(node2a)[circ]{} -- ++(-1, 0) node[ground, rotate=270]{};
		\draw (node1a) -- ++(2, 0) node(node1b)[circ]{} -- ++(0, -4) node(node2b)[circ]{} -- (node2a);
		\draw (node1b) -- ++(2, 0) node(node1c)[circ]{} to[capacitor, l_=C2, a^=\SI{1}{\micro\farad}] ++(0, -4) node(node2c)[circ]{} -- (node2a);
		\draw (node1c) -- ++(2, 0) node(node1d)[circ]{} to[resistor, l_=R1, a^=\SI{100}{\ohm}] ++(0, -2) to[capacitor, l_=C3, a^=\SI{10}{\nano\farad}] ++(0, -2) node(node2d)[circ]{} -- (node2c);
		\draw (node1d) -- ++(2, 0) node(node1e)[circ]{} to[ecapacitor, l_=C4, a^=\SI{22}{\micro\farad}] ++(0, -4) node(node2e)[circ]{} -- (node2c);
		\draw (node1e) -- ++(1, 0) node[vcc, rotate=270, label={[label distance=6]:\SI{10}{\volt}}]{};
		\draw (node2e) -- ++(1, 0) node[ground, rotate=90]{};
		% TODO: use dipchip node and name IC ports
		\begin{scope}[xshift=4cm]
			\node[draw, rectangle, fill=white, minimum width=3cm, minimum height=1.4cm, label=above:U1]{};
			\node at (0, 0) {REF5010};
		\end{scope}
	\end{circuitikz}
	\caption{High-precision voltage reference.}\label{fig:voltage_reference}
\end{figure}
\Cref{fig:voltage_reference} depicts the schematic of the voltage reference circuit.
Capacitor C1 buffers the \SI{15}{\volt} supply voltage.
According to the datasheet the trim terminal should be connected through a capacitor, C2, to ground.
Resistor R1 and capacitor C3 form a low-pass to suppress frequency components in the kHz range.
Finally, capacitor C4 buffers the output voltage.

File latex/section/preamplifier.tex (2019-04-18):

\section{Preamplifier}

The photocurrents created by our detector are in the range of microampere where they are vulnerable to noise.
Using a preamplifier, we can increase the amplitude of the signal for an improved signal-to-noise ratio.
The typical photocurrent preamplifier is based on the transimpedance (current-to-voltage) amplifier design using a voltage-feedback operational amplifier.
Converting the current to a voltage signal has the benefit that the voltage signal can be easily visualized with an oscilloscope.
Furthermore, the voltage-feedback operational amplifier design appears to be more common than the current-feedback operational amplifier, as manufacturers offer much more choice and they are more prominent in the literature.
That said, current-feedback operational amplifiers are reported to be a viable solution for high-speed and high-bandwidth applications, see Ref.~\cite[p.~110]{Jung05} for an overview of the benefits of current-feedback amplifiers and Ref.~\cite[Ch.~9]{Carter17} for a comparison with voltage-feedback amplifiers.
An embodiment of current-feedback operational amplifiers for high-accuracy applications can be found in Ref.~\cite[p.~143]{Noorlag74}.

In the following, we will always refer to the voltage-feedback operational amplifier if not noted otherwise.
Moreover, we expect the reader to be familiar with the foundations of the operational amplifier.
Well-written introductions to this topic can be found in \cite[Ch.~1]{Jung05} and \cite[Ch.~3]{Carter17}.

\subsection{Basic design}

The basic design of a transimpedance amplifier is illustrated in~\Cref{fig:basic_transimpedance}.
Ignoring imperfections of the photodiode, we can represent the photodiode as a current source.
The non-inverting input of the operational amplifier is connected to ground.
The inverting input is coupled with the output of the operational amplifier via a feedback impedance $Z_f$.
\begin{figure}[H]
	\centering
	\begin{circuitikz}
		\draw (0, 0) node[op amp](opamp){};
		\draw (opamp.+) -- +(0, -1) node[ground](gnd1){};
		\draw (opamp.out) -- +(1, 0) node[ocirc, label=$V_\text{out}$]{};
		\draw (opamp.-) node[circ]{} -- +(-2, 0) node(node1){} to[current source, invert, l=$I_\text{in}$] (node1 |- gnd1) node[ground]{};
		\draw (opamp.-) |- (-1, 2) to[generic, l=$Z_f$] (1,2) -| (opamp.out);
	\end{circuitikz}
	\caption{Basic transimpedance amplifier using voltage feedback operational amplifier.}\label{fig:basic_transimpedance}
\end{figure}
The ideal operation amplifier has zero input current, thus, in the node of the inverting input of the operational amplifier Kirchhoff's law states that the current going through the feedback impedance has to cancel the current of the current source $I_\text{in}$.
The current through the feedback impedance $Z_f$ can be expressed in terms of the feedback impedance $Z_f$ and the output voltage $V_\text{out}$ of the operational amplifier through the use of Ohm's law, yielding,
\begin{equation}
	V_\text{out}=-Z_fI_\text{in}
	\label{eq:transimpedance}.
\end{equation}
Given a maximum current $I_\text{in}$ and a desired maximum output voltage $V_\text{out}$, \Cref{eq:transimpedance} determines the feedback impedance.
Limitations arise for real operational amplifiers where the output voltage is limited to be below the supply voltage of the operational amplifier.

Aside from photodiode applications, it is more common to find the inverting (voltage-to-voltage) operational amplifier in the literature.
By using the source transformation on the current source with a parallel impedance in the transimpedance amplifier circuit, we can recover the inverting operational amplifier circuit, and thereby easily use results obtained for the inverting amplifier design.
\begin{figure}[H]
	\begin{subfigure}[t]{.5\textwidth}
		\centering
		\begin{circuitikz}
			\draw (0, 0) node[op amp](opamp){};
			\draw (opamp.+) -- +(0, -1) node[ground](gnd1){};
			\draw (opamp.out) -- +(1, 0) node[ocirc, label=$V_\text{out}$]{};
			\draw (opamp.-) node[circ]{} -- +(-3, 0) node(node1){} to[current source, invert, l=$I_\text{in}$] (node1 |- gnd1) node[ground]{};
			\draw (opamp.-) node[circ]{} -- +(-1.5, 0) node(node1){} to[generic, invert, l=$Z_\text{in}$] (node1 |- gnd1) node[ground]{};
			\draw (opamp.-) |- (-1, 2) to[generic, l=$Z_f$] (1,2) -| (opamp.out);
		\end{circuitikz}
		\caption{Transimpedance amplifier.}
	\end{subfigure}
	\begin{subfigure}[t]{.5\textwidth}
		\centering
		\begin{circuitikz}
			\draw (0, 0) node[op amp](opamp){};
			\draw (opamp.+) -- +(0, -1) node[ground](gnd1){};
			\draw (opamp.out) -- +(1, 0) node[ocirc, label=$V_\text{out}$]{};
			\draw (opamp.-) node[circ]{} to[generic, invert, l_=$Z_\text{in}$] +(-3, 0) node(node1){} to[voltage source, l=$V_\text{in}{=}Z_\text{in}I_\text{in}$] (node1 |- gnd1) node[ground]{};
			\draw (opamp.-) |- (-1, 2) to[generic, l=$Z_f$] (1,2) -| (opamp.out);
		\end{circuitikz}
		\caption{Inverting amplifier.}
	\end{subfigure}
	\caption{Equivalence between transimpedance and inverting amplifier using source transformation.}\label{fig:equivalence_transimpedance_inverting}
\end{figure}
\Cref{fig:equivalence_transimpedance_inverting} shows the source transformation applied to transimpedance and inverting amplifier circuits.
Given a current source $I_\text{in}$ with parallel impedance $Z_\text{in}$ the equivalent voltage source has value $V_\text{in}=Z_\text{in}I_\text{in}$ with impedance $Z_\text{in}$ in series.

\subsection{Input offset voltage}

Real operational amplifiers only reduce the voltage difference between the inverting and non-inverting input to a non-zero input offset voltage.
For high-precision operational amplifiers, the input offset voltage is in the range of microvolts.
We can model the input offset voltage as a voltage source at the non-inverting input of an ideal operational amplifier in our transimpedance circuit, as can be seen from \Cref{fig:input_offset_voltage_transimpedance}.
In \Cref{fig:input_offset_voltage_transimpedance} we amended the basic transimpedance circuit of \Cref{fig:basic_transimpedance} by inserting a voltage source with the input offset voltage between the non-inverting input and ground.
\begin{figure}[H]
	\centering
	\begin{circuitikz}
		\draw (0, 0) node[op amp](opamp){};
		\draw (opamp.-) |- (-1, 2) to[generic, l=$Z_f$] (1,2) -| (opamp.out);
		\draw (opamp.out) -- +(1, 0) node[ocirc, label=$V_\text{out}$]{};
		\draw (opamp.+) -- ++(0, -.5) node(node1){} to[voltage source, l=$V_\text{offset}$] ++(0, -2) node[ground](gnd1){};
		\draw (opamp.-) node[circ]{} -- +(-2, 0) node(node2){} -- (node2 |- node1) to[current source, invert, l=$I_\text{in}$] (node2 |- gnd1) node[ground]{};
	\end{circuitikz}
	\caption{Input offset voltage in the transimpedance amplifier.}\label{fig:input_offset_voltage_transimpedance}
\end{figure}
In order to estimate the output offset $V_\text{out}$ caused by the input offset voltage $V_\text{offset}$ we adapt the picture of the inverting amplifier.
\Cref{fig:input_offset_voltage_inverting} shows an inverting amplifier circuit with input impedance $Z_\text{in}$ and input offset voltage $V_\text{offset}$ at the non-inverting input of the operational amplifier.
According to the superposition theorem, we can replace the input voltage source with a short circuit to estimate the contribution of the input offset voltage source.
\begin{figure}[H]
	\centering
	\begin{circuitikz}
		\draw (0, 0) node[op amp](opamp){};
		\draw (opamp.-) |- (-1, 2) to[generic, l=$Z_f$] (1,2) -| (opamp.out);
		\draw (opamp.out) -- +(1, 0) node[ocirc, label=$V_\text{out}$]{};
		\draw (opamp.+) -- ++(0, -.5) node(node1){} to[voltage source, l=$V_\text{offset}$] ++(0, -2) node[ground](gnd1){};
		\draw (opamp.-) node[circ]{} -- +(-2, 0) node(node2){} -- (node2 |- node1) to[generic, l=$Z_\text{in}$] (node2 |- gnd1) node[ground]{};
	\end{circuitikz}
	\caption{Input offset voltage in the inverting amplifier.}\label{fig:input_offset_voltage_inverting}
\end{figure}
From \Cref{fig:input_offset_voltage_inverting} we identify input and feedback impedance as a voltage divider in which the input and output nodes are exchanged.
The respective transfer function reads,
\begin{equation}
	V_\text{out}=-\frac{R_f+R_\text{in}}{R_\text{in}}V_\text{offset}=-\left(1+\frac{R_f}{R_\text{in}}\right)V_\text{offset}
	\label{eq:input_offset_voltage}.
\end{equation}
Comparing \Cref{eq:input_offset_voltage} with \Cref{eq:transimpedance} discloses a difference in gain.
The gain of the input signal in Eq. 1 is commonly referred to as signal gain. 
The gain of a signal applied directly to the inputs of the operational amplifier is referred to as noise gain.
In the case of the position-sensitive detector, the input resistance is of order \SI{10}{\kilo\ohm}.
Using a feedback resistance of $R_f=\SI{100}{\kilo\ohm}$ we find that the input offset voltage experiences a gain of 11.

One approach to compensate for the input offset voltage as described is depicted in \Cref{fig:input_offset_voltage_compensation}, see also Ref~\cite[p.~54]{Jung05}.
A potentiometer with maximum resistance Rp connects the positive and negative supply voltage.
The wiper of the potentiometer is connected with a first resistor R1 to a node.
The node is connected with a second resistor R2 and an optional bypass capacitor to ground.
Finally, the equivalent input offset voltage source connects the node with the non-inverting input of the operational amplifier.
\begin{figure}[H]
	\centering
	\begin{circuitikz}
		\draw (0, 3) node[ocirc, label=$+V_\text{supply}$]{} to[potentiometer, n=poti, l_=$R_p$] ++(0, -3) node[ocirc, label=$-V_\text{supply}$, rotate=180]{};
		\draw (poti.wiper) to[resistor, l=$R_1$] ++(2, 0) node(node1)[circ]{} to[resistor, l=$R_2$] ++(0, -2) node(gnd)[ground]{};
		\draw (node1) to[voltage source, l_=$V_\text{offset}$, invert] ++(0, 2) node[ocirc, label=$V_+$]{};
		\draw (node1) -- ++(2, 0) to[capacitor, l=$C_1$] ++(0, -2) node[ground]{};
	\end{circuitikz}
	\caption{Input offset voltage compensation using adjustable potentiometer.}\label{fig:input_offset_voltage_compensation}
\end{figure}
Let $0\leq x\geq1$ be the position of the potentiometer.
For $x=1/2$ the resistance of the potentiometer is $R_p/2$ and there is no offset compensation.
For $x<1/2$ the input offset compensation is negative to compensate for a positive input offset voltage.
For $x>1/2$ the input offset compensation is positive to compensate for a negative input offset voltage.
The maximum input offset compensation is obtained for $x=0$ and $x=1$.
Using circuit analysis techniques, we obtain,
\begin{equation}
	V_c(x)=\frac{R_2(1-2x)}{R_1+R_2-R_p(1-x)x}V_\text{supply},
\end{equation}
as an analytical expression for the input offset voltage compensation measured between the node and ground.
The maximum absolute value of the compensation voltage follows to be,
\begin{equation}
	V_c(0)=V_c(1)=\pm\frac{R_2}{R_1+R_2}V_\text{supply}.
\end{equation}
Given a maximum input offset voltage of \SI{100}{\micro\volt} and a supply voltage of \SI{15}{\volt}, we find approximate resistor values $R_1=\SI{3}{\mega\ohm}$ and $R_2=\SI{2}{\ohm}$.
The resistor value of the potentiometer $R_p$ should be chosen sufficiently large such to limit the current.
For example, a potentiometer resistance of $R_p=\SI{15}{\kilo\ohm}$ would limit the current to \SI{2}{\milli\ampere} with a heat dissipation of \SI{60}{\milli\watt}.
In practice, one should aim for a slightly higher maximum compensation voltage in order to handle resistor mismatches.

That said, there are some practical arguments against the use of the described input offset voltage compensation.
The first argument is that the low resistance of $R_2$ acts as a dominant source for thermal current noise density of about \SI{100}{\pico\ampere\per\sqrt\hertz}.
As this current noise contributes to the input of the transimpedance amplifier it gets amplified by the feedback impedance $Z_f$, yielding up to \SI{110}{\micro\volt\per\sqrt\hertz} in voltage noise density, which --- depending on the bandwidth --- surpasses the actual input offset voltage to compensate.
The second argument is that high-precision potentiometers with large dynamic range get very large and difficult to accommodate on a printed circuit board.

\subsection{Input bias current}

In addition to the input offset voltage $V_\text{offset}$, there is a second effect that causes an offset in the output voltage $V_\text{out}$.
This second effect stems from the small amount of current that is drawn from the inputs of the operational amplifier.
We highlighted the input currents in \Cref{fig:input_bias_current} where they are represented by the current flows $i_+$ and $i_-$ directly pointing into the inputs of the operational amplifier in the transimpedance circuit.
\begin{figure}[H]
	\centering
	\begin{circuitikz}
		\draw (0, 0) node[op amp](opamp){};
		\draw (opamp.out) -- +(0.5, 0) node(node1)[circ]{} -- ++(1.5, 0) node[ocirc, label=$V_\text{out}$]{};
		\draw (opamp.-) to[short, i<_=$i_-$] ++(-1, 0) node(node1a)[circ]{} |- (-1.5, 2) to[generic, l=$Z_f$] (1.5, 2) -| (node1);
		\draw (opamp.+) to[short, i<_=$i_+$] ++(-1, 0) node(node1b){} -- ++(0, -1) node(gnd)[ground]{};
		\draw (node1a) -- ++(-1.5, 0) node(node2a){} to[current source, invert, l=$I_\text{in}$] (node2a |- gnd) node[ground]{};
	\end{circuitikz}
	\caption{Input bias current offset in the transimpedance amplifier.}\label{fig:input_bias_current}
\end{figure}
Input bias currents for high-precision operational amplifier are in the range of picoamperes.
These small currents are usually difficult to measure and may differ between inputs.
The datasheet of the operational amplifier, therefore, doesn't report the input bias current per terminal but the mean $I_\text{bias}$ and the difference between the input currents $I_\text{offset}$.
The relationship between the mean input bias current $I_\text{bias}$ and the input offset current $I_\text{offset}$ with respect to the actual input bias currents $i_+,i_-$ is given below.
\begin{align}
	i_+=I_\text{bias}+\frac{1}{2}I_\text{offset} &&
	I_\text{offset}=i_+-i_- \\
	i_-=I_\text{bias}-\frac{1}{2}I_\text{offset} &&
	I_\text{bias}=\frac{i_++i_-}{2}
\end{align}
According to Ref.~\cite[p.~57]{Jung05} and Ref.~\cite[p.~25]{Graeme96} the effect of the input bias currents $i_+,i_-$ on the output voltage $V_\text{out}$ can be compensated with an impedance $Z_c$ at the non-inverting input of the operational amplifier.
\Cref{fig:input_bias_current_compensation} illustrates the inverting amplifier configuration with such a compensation impedance $Z_c$.
\begin{figure}[H]
	\centering
	\begin{circuitikz}
		\draw (0, 0) node[op amp](opamp){};
		\draw (opamp.out) -- +(0.5, 0) node(node1)[circ]{} -- ++(1.5, 0) node[ocirc, label=$V_\text{out}$]{};
		\draw (opamp.-) to[short, i<_=$i_-$] ++(-1, 0) node(node1a)[circ]{} |- (-1.5, 2) to[generic, l=$Z_f$] (1.5, 2) -| (node1);
		\draw (opamp.+) to[short, i<_=$i_+$] ++(-1, 0) node(node1b){} to[generic, l=$Z_c$] ++(0, -2) node(gnd)[ground]{};
		\draw (node1a) -- ++(-1.5, 0) node(node2a){} -- (node1b -| node2a) to[generic, l=$Z_\text{in}$] (node2a |- gnd) node[ground]{};
	\end{circuitikz}
	\caption{Input current offset compensation.}\label{fig:input_bias_current_compensation}
\end{figure}
Following the argumentation from Ref.~\cite[p.~383]{Terrel96}, the input bias current at the inverting input of the operational amplifier $i_-$ develops a voltage of $Z_fi_-$ over the feedback impedance $Z_f$.
The input bias current at the non-inverting input $i_-$ develops the voltage $Z_ci_-$ over the compensation resistor $Z_c$.
The voltage $Z_ci_-$ propagates through the voltage divider comprising the feedback and input impedance analogue to the input offset voltage.
According to the superposition theorem, both of these contributions add and yield,
\begin{equation}
	V_\text{out}=i_+Z_c\left(1+\frac{Z_f}{Z_\text{in}}\right)-i_-Z_f
	\label{eq:input_bias_current},
\end{equation}
at the output voltage.
If $i_+\approx i_-$ we can choose,
\begin{equation}
	Z_c=\frac{Z_\text{in}}{Z_\text{in}+Z_f},
\end{equation}
 to compensate for the output voltage offset caused by the input bias currents.
The condition $i_+\approx i_-$ is usually satisfied if the input offset current $I_\text{offset}$ reported in the datasheet is less than the mean input bias current $I_\text{bias}$.
High-precision operational amplifier usually have compensated bias currents that do not satisfy this condition.
In this case, there is no generic formula for the value of the compensation impedance $Z_c$ in terms of input and feedback impedance and one needs to perform impedance matching on a per-device basis.
One should keep in mind that high-precision operational amplifier have input bias currents in the range of \si{\pico\ampere}.
Using \Cref{eq:input_bias_current} one should therefore first check if the output voltage offset due to input bias currents is even worth compensating compared to other offset and noise contributions.

\subsection{Stability and bandwidth}

The outputs of the transimpedance and inverting amplifier designs have a phase shift of \SI{180}{\degree}.
If an additional phase shift of \SI{180}{\degree} accumulates because of the inherent bandwidth limitations of the operational amplifier and the gain is equal or greater than unity, the conditions for oscillations are met and the amplifier will become unstable, see Ref.~\cite[p.~395]{Terrel96}.
By artificially limiting the bandwidth with an additional frequency pole, we can flatten out the frequency response at high frequencies, and thereby stabilize the amplifier, see Ref.~\cite[p.~184]{Kay12}.

\Cref{fig:bode_gain} shows a Bode plot of the open-loop (black) and noise gain (red) of an operational amplifier.
The noise gain separates into a compensated (solid) and uncompensated (dotted) branch.
\begin{figure}[H]
	\centering
	\begin{tikzpicture}[scale=1.2, transform shape]
		\begin{semilogxaxis}[xmin=1, xmax=1e9, xlabel=Frequency (Hz), ymin=0, ymax=140, ylabel=Gain (dB), ytick={0, 20, 40, 60, 80, 100, 120, 140}, grid=minor]
			\addplot[domain=1:1e2]{120};
			\addplot[domain=1e2:1e9]{160-20*log10(x)};
			\addplot[domain=1:1e4, color=red]{40};
			\addplot[domain=1e4:1e5, color=red]{-40+20*log10(x)};
			\addplot[domain=1e5:1e9, color=red]{60};
			\addplot[domain=1e5:1e9, dashed, color=red]{-40+20*log10(x)};
		\end{semilogxaxis}
		\node[label={AOL}] at (.8, 4.1) {};
		\node[label={[red]$1/\beta$}] at (.8, .7) {};
		\node[label={[red]compensated}] at (5.5, 1.7) {};
		\node[label={[red]uncompensated}] at (4.2, 4) {};
	\end{tikzpicture}
	\caption{Bode plot of the open-loop and closed-loop gain of the amplifier.}\label{fig:bode_gain}
\end{figure}
With the uncompensated branch we would observe instability due to oscillations.
The compensated branch is obtained through addition of a feedback capacitor.
According to Ref.~\cite[p.~113]{Jung05}, Ref.~\cite[p.~693]{Hobbs11} and Ref.~\cite[Ch.~3]{Graeme96} the value for the feedback capacitance is given by,
\begin{equation}
	C_f\geq\sqrt{\frac{C_\text{in}}{2\pi R_f f_u}}
	\label{eq:feedback_capacitance_approximation},
\end{equation}
wherein $R_f$ denotes the feedback resistance and $f_u$ the unity-gain-bandwidth of the operational amplifier.
The capacitance should be chosen larger to ensure design margin.
The unity-gain-bandwidth of the operational amplifier denotes the frequency where the open-loop gain equals unity and is reported in the datasheet as \gls{gbp} of the operational amplifier.
$C_\text{in}$ in \Cref{eq:feedback_capacitance_approximation} represents the sum of the input capacities of the amplifier circuit and the capacitance of the signal source.
According to Ref.~\cite[p.~185]{Carter17} a more exact formula for the feedback capacitance is given by,
\begin{align}
	C_f\geq\frac{C_\text{aux}}{2}\left(1+\sqrt{1+\frac{4C_\text{in}}{C_\text{aux}}}\right) &&
	C_\text{aux}=\frac{1}{2\pi R_f f_u}
	\label{eq:feedback_capacitance_exact},
\end{align}
which is also valid if not $C_\text{in}\gg C_f$.

\Cref{fig:capacitive_transimpedance} illustrates the transimpedance amplifier with capacitive elements.
Parallel to the current source $I_\text{in}$ we find the input capacitance $C_\text{in}$ comprising source capacitance and operational amplifier capacitance.
Parallel to the feedback resistance $R_f$ we find the feedback capacitance $C_f$ with value given in \Cref{eq:feedback_capacitance_exact} or \Cref{eq:feedback_capacitance_approximation}.
\begin{figure}[H]
	\centering
	\begin{circuitikz}
		\draw (0, 0) node[op amp](opamp){};
		\draw (opamp.+) -- +(0, -1) node[ground](gnd1){};
		\draw (opamp.out) -- +(1, 0) node[ocirc, label=$V_\text{out}$]{};
		\draw (opamp.-) node[circ]{} -- +(-4, 0) node(node1){} to[current source, invert, l=$I_\text{in}$] (node1 |- gnd1) node[ground]{};
		\draw (opamp.-) node[circ]{} -- +(-2, 0) node(node1){} to[capacitor, l=$C_\text{in}$] (node1 |- gnd1) node[ground]{};
		\draw (opamp.-) |- (-1, 2) to[resistor, l=$R_f$] (1, 2) -| (opamp.out);
		\draw (opamp.-) |- (-1, 3.5) to[capacitor, l=$C_f$] (1, 3.5) -| (opamp.out);
	\end{circuitikz}
	\caption{Transimpedance amplifier with capacitive elements.}\label{fig:capacitive_transimpedance}
\end{figure}
% TODO: why use noise gain
% TODO: definition open-loop gain, closed-loop gain
% TODO: why is rate of closure important for stability (relation with phase margin?)

As noted earlier, the bandwidth is reduced through the additional feedback capacitor.
The new bandwidth is now given by the RC pole formed by the feedback impedance,
\begin{equation}
	BW=\frac{1}{2\pi R_fC_f}.
\end{equation}
Given a unity-gain-bandwidth of the operational amplifier of $f_u=\SI{10}{\mega\hertz}$ and a feedback resistance of $R_f=\SI{100}{\kilo\ohm}$ \Cref{eq:feedback_capacitance_approximation} yields a minimum feedback capacitance of $C_f=\SI{4}{\pico\farad}$.
Together with $R_f$ this feedback capacitance limits the bandwidth to about \SI{400}{\kilo\hertz}.

\subsection{Signal-to-noise ratio}

% TODO: (Jung, p. 80)
% TODO: thermal noise from resistor
% TODO: equivalent noise from operational amplifier

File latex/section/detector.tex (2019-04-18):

\section{Position-sensitive detector}

\subsection{Transverse photoeffect}

The purpose of the following section is to recall the mechanics of the (transverse) photoeffect observed in an illuminated p-n junction.
Figures and the description thereof is largely based on Ref.~\cite{Simon13}.
A subtle difference in the depicted figures and the figures of Ref.~\cite{Simon13} is that we exchanged the order of p- and n-type semiconductors.
We found this order to be more intuitive when referring to a p-n junction.

\Cref{fig:pn_junction_separated} shows a separated p- and n-type semiconductor.
In the upper half, we see an illustration of the p- and n-type semiconductor with their respective mobile charge carriers.
The p-type semiconductor has an excess of positive charge carriers (holes) which are depicted as white circles.
The n-type semiconductor has an excess of negative charge carriers (electrons) which are depicted as black circles.
The excess charge carriers form due to the implantation of acceptor and donator ions.
These are depicted as circles with plus and minus sign in \Cref{fig:pn_junction_separated}.
The implanted ions have more or fewer electrons than the atoms of the semiconductor material.
Therefore donating an electron or accepting an electron and effectively forming a hole as an absence of negative charge.
\begin{figure}[H]
	\centering
	\begin{tikzpicture}
		\draw (1.5, 2.5) node {p-type};
		\draw (5, 2.5) node {n-type};
		\filldraw[draw=black, fill=gray] (0, 0) rectangle (3, 2);
		\filldraw[draw=black, fill=gray!40] (3.5, 0) rectangle (6.5, 2);
		\foreach \x in {1, ..., 4} {
			\filldraw[fill=white] (0.25+0.5*\x, 0.4) circle (.1);
			\filldraw[fill=white] (0.25+0.5*\x, 1.2) circle (.1);

			\filldraw[fill=black] (3.75+0.5*\x, 0.8) circle (.1);
			\filldraw[fill=black] (3.75+0.5*\x, 1.6) circle (.1);
		}
		\foreach \x in {1, ..., 5} {
			\filldraw[fill=white] (0.5*\x, 0.8) circle (.1);
			\filldraw[fill=white] (0.5*\x, 1.6) circle (.1);
			
			\filldraw[fill=black] (3.5+0.5*\x, 0.4) circle (.1);
			\filldraw[fill=black] (3.5+0.5*\x, 1.2) circle (.1);
		}
		\foreach \x in {0, ..., 5} {
			\draw (0.25+0.5*\x, -0.3) node[circle, draw=black, inner sep=0]{$-$};
			\draw (3.75+0.5*\x, -0.3) node[circle, draw=black, inner sep=0]{$+$};
		}
		\draw[-latex] (-0.5, -5) -- (-0.5, -2) node[left]{$E$};
		\draw[dotted, line width=1] (3.25, -2) -- (3.25, -5);
		\filldraw[draw=black, fill=gray] (0, -2) rectangle +(3, -1) +(0, -1.8) node[left]{$\mu$} -- +(3, -1.8) ++(0, -2) rectangle +(3, -1);
		\filldraw[draw=black, fill=gray!40] (3.5, -2) rectangle +(3, -1) +(0, -1.2) -- +(3, -1.2) node[right]{$\mu$} ++(0, -2) rectangle +(3, -1);
		\draw (3.25, -1.6) node{conduction band} +(0, -3.8) node{valence band};
		\foreach \x in {0, ..., 6} {
			\filldraw[fill=white] (0.3+0.4*\x, -4.2) circle (.11);
			\filldraw[fill=black] (3.8+0.4*\x, -2.8) circle (.09);
		}
	\end{tikzpicture}
	\caption{Separated p- and n-type semiconductor with holes (white) and electrons (black).}\label{fig:pn_junction_separated}
\end{figure}
The lower half of \Cref{fig:pn_junction_separated} shows the energy band structure of both p- and n-type semiconductor.
The lower energy band represents the valence band made up of the electrons that are tightly bound to a single atomic core.
The upper energy band represents the conduction band made up of electrons that are are not bound to a single atomic core but shared across the lattice.
Charge carriers in the conduction band can move freely and thereby contribute to the conductivity of the material.
For an undoped (intrinsic) semiconductor the chemical potential is in the center of the band gap between the conduction and valence band.
Through doping, the chemical potential is shifted in the p- and n-type semiconductor.
In the p-type semiconductor, acceptor ions can take up electrons from the conduction band, thereby decreasing the chemical potential.
In the n-type semiconductor, donator ions contribute electrons to the conduction band, thereby increasing the chemical potential.
\begin{figure}[H]
	\centering
	\begin{tikzpicture}
		\draw (1.5, 2.5) node {p-type};
		\draw (5, 2.5) node {n-type};
		\filldraw[draw=black, fill=gray] (0, 0) rectangle (3, 2);
		\filldraw[draw=black, fill=gray!40] (3, 0) rectangle (6, 2);
		\foreach \x in {1, ..., 4} {
			\filldraw[fill=white] (0.25+0.5*\x, 0.4) circle (.1);
			\filldraw[fill=white] (0.25+0.5*\x, 1.2) circle (.1);

			\filldraw[fill=black] (3.75+0.5*\x, 0.8) circle (.09);
			\filldraw[fill=black] (3.75+0.5*\x, 1.6) circle (.09);
		}
		\foreach \x in {1, ..., 4} {
			\filldraw[fill=white] (0.5*\x, 0.8) circle (.1);
			\filldraw[fill=white] (0.5*\x, 1.6) circle (.1);
			
			\filldraw[fill=black] (3.5+0.5*\x, 0.4) circle (.09);
			\filldraw[fill=black] (3.5+0.5*\x, 1.2) circle (.09);
		}
		\foreach \x in {0, ..., 5} {
			\draw (0.25+0.5*\x, -0.3) node[circle, draw=black, inner sep=0]{$-$};
			\draw (3.25+0.5*\x, -0.3) node[circle, draw=black, inner sep=0]{$+$};
		}
		\draw[dashed, line width=.8] (2.5, -.5) -- +(0, 2.5) +(1, 0) -- +(1, 2.5) +(0.5, -0.3) node{depletion region};

		\draw[-latex] (-0.5, -5) -- (-0.5, -2) node[left]{$E$};
		\filldraw[draw=black, fill=gray] (0, -2) rectangle +(3, -1) +(0, -1.8) node[left]{$\mu$} -- +(2.5, -1.8) ++(0, -2) rectangle +(3, -1);
		\filldraw[draw=black, fill=gray!40] (3, -2) rectangle +(3, -1) +(0.5, -1.2) -- +(3, -1.2) node[right]{$\mu$} ++(0, -2) rectangle +(3, -1);
		\draw[dashed, line width=.8] (2.5, -5) -- +(0, 3) +(1, 0) -- +(1, 3) +(0.5, -0.3);
		\draw (3, -1.6) node{conduction band} +(0, -3.8) node{valence band};
		\foreach \x in {0, ..., 5} {
			\filldraw[fill=white] (0.3+0.4*\x, -4.2) circle (.10);
			\filldraw[fill=black] (3.7+0.4*\x, -2.8) circle (.09);
		}
		
		\draw[-latex] (-0.5, -8) -- (-0.5, -6) node[left]{$-e\phi$};
		\draw (0, -6.5) -- ++(2.5, 0) -- ++(1, -1) -- ++(2.5, 0);
		\draw (3, -8) node{electrostatic potential};
	\end{tikzpicture}
	\caption{Combined p- and n-type semiconductor with holes (white) and electrons (black).}\label{fig:pn_junction_combined}
\end{figure}
In \Cref{fig:pn_junction_combined} the p- and n-type semiconductor are brought into contact with each other, forming a p-n junction.
In close proximity of the junction holes and energies recombine due to a diffusion process, leaving an electrically charged area.
The electrically charged area creates an electrostatic potential across the junction as illustrated in the lower part of \Cref{fig:pn_junction_combined}.
We refer to this area as the depletion region.
In \Cref{fig:pn_junction_combined} the depletion region expands between the dashed lines around the junction.
\begin{figure}[H]
	\centering
	\begin{tikzpicture}
		\draw (1.25, 3.6) node {p-type};
		\draw (4.75, 3.0) node {n-type};
		\draw[-latex] (-0.5, -0.5) -- (-0.5, 3.5) node[left]{$E-e\phi$};
		\filldraw[draw=black, fill=gray] (0, 3.3) rectangle +(2.5, -1) +(0, -1.8) node[left]{$\mu$} -- +(2.5, -1.8) ++(0, -2) rectangle +(2.5, -1);
		\filldraw[draw=black, fill=gray!40] (3.5, 2.7) rectangle +(2.5, -1) +(0, -1.2) -- +(2.5, -1.2) node[right]{$\mu$} ++(0, -2) rectangle +(2.5, -1);
		\filldraw[draw=black, fill=gray!70] (2.5, 3.3) -- ++(1, -.6) -- ++(0, -1) -- ++(-1, .6) -- ++(0, 1);
		\filldraw[draw=black, fill=gray!70] (2.5, 1.3) -- ++(1, -.6) -- ++(0, -1) -- ++(-1, .6) -- ++(0, 1);
		\draw[-latex] (4.5, 0.7) -- ++(0, 0.8);
		\draw (4.5, 1.05) node[right]{$E_\text{gap}$};
		\foreach \x in {0, ..., 5} {
			\filldraw[fill=white] (0.25+0.4*\x, 1.1) circle (.10);
			\filldraw[fill=white] (3.75+0.4*\x, 0.5) circle (.10);
			\filldraw[fill=black] (3.75+0.4*\x, 1.9) circle (.09);
			\filldraw[fill=black] (0.25+0.4*\x, 2.5) circle (.09);
		};
		\filldraw[fill=white] (2.8, 0.9) circle (.10);
		\filldraw[fill=white] (3.2, 0.65) circle (.10);
		\filldraw[fill=black] (2.8, 2.3) circle (.09);
		\filldraw[fill=black] (3.2, 2.1) circle (.09);
	\end{tikzpicture}
	\caption{Energy bands of the p-n junction.}\label{fig:pn_junction}
\end{figure}
The energy band diagram in \Cref{fig:pn_junction} accounts for the shift in energy due to the electrostatic potential.
The chemical potentials of both sides of the junction are now aligned.
The energy required to excite an electron on the p-type side from the valence to the conduction band and the energy required to excite a hole from the conduction to the valence band are equal to the band gap of the semiconductor.

% TODO: motivate reverse bias (photoconductive mode) vs. unbiased (photovoltaic) mode by measurement vs. energy conversion application 
If one applies a reverse bias voltage across the p-n junction, the effective energy gap between conduction and valence band is reduced, the electrostatic potential increases and the depletion region broadens.
The situation of an applied reverse voltage is depicted in \Cref{fig:pn_junction_reverse}.
\begin{figure}[H]
	\centering
	\begin{tikzpicture}
		\draw (1, 3.6) node {p-type};
		\draw (5, 2.2) node {n-type};
		\draw[-latex] (-0.5, -1) -- (-0.5, 3.8) node[left]{$E-e\phi$};
		\filldraw[draw=black, fill=gray] (0, 3.3) rectangle +(2, -1) +(0, -1.5) node[left]{$\mu$} -- +(2, -1.5) ++(0, -1.6) rectangle +(2, -1);
		\filldraw[draw=black, fill=gray!40] (4, 1.9) rectangle +(2, -1) +(0, -1.1) -- +(2, -1.1) node[right]{$\mu-eV$} ++(0, -1.6) rectangle +(2, -1);
		\filldraw[draw=black, fill=gray!70] (2, 3.3) -- ++(2, -1.4) -- ++(0, -1) -- ++(-2, 1.4) -- ++(0, 1);
		\filldraw[draw=black, fill=gray!70] (2, 1.7) -- ++(2, -1.4) -- ++(0, -1) -- ++(-2, 1.4) -- ++(0, 1);
		\draw[-latex] (4.2, 0.3) -- ++(0, 0.5);
		\draw (4.2, 0.5) node[right]{$E_\text{gap}-eV$};
		\foreach \x in {0, ..., 4} {
			\filldraw[fill=white] (0.2+0.4*\x, 1.5) circle (.10);
			\filldraw[fill=white] (2.2+0.4*\x, 1.3-0.275*\x) circle (.10);
			\filldraw[fill=white] (4.2+0.4*\x, 0.1) circle (.10);
			\filldraw[fill=black] (4.2+0.4*\x, 1.1) circle (.09);
			\filldraw[fill=black] (2.2+0.4*\x, 2.4-0.275*\x) circle (.09);
			\filldraw[fill=black] (0.2+0.4*\x, 2.5) circle (.09);
		};
	\end{tikzpicture}
	\caption{Energy band diagram of a reverse biased p-n junction.}\label{fig:pn_junction_reverse}
\end{figure}
The current-voltage characteristic of the p-n junction is described by the Schockley diode equation,
\begin{equation}
	I_\text{diode}=I_\text{sat}(T)\left(e^{eV/k_BT}-1\right)
	\label{eq:diode_current},
\end{equation}
wherein $I_\text{sat}\propto e^{-E_\text{gap}/k_BT}$ is the temperature dependent reverse bias saturation current and $V$ the voltage applied to the p-n junction.
Using the proportionality of the reverse bias saturation current, we can write,
\begin{equation}
	I_\text{diode}\propto e^{\left(eV-E_\text{gap}\right)/k_BT}-e^{-E_\text{gap}/k_BT}\label{eq:diode_current_prop},
\end{equation} 
which discloses the two effects contributing to the diode current.
The left-hand side of the proportionality of \Cref{eq:diode_current_prop} represents the current contribution due intra-band excitation of charge carriers, whereas the right-hand side represents the current contribution due to inter-band excitation.
\begin{figure}[H]
	\centering
	\begin{tikzpicture}
		\begin{axis}[xmin=-5, xmax=5, xticklabels=\empty, xlabel=$V$, ymin=-5, ymax=5, ylabel=$I$, yticklabels=\empty, axis lines=middle]
			\addplot[domain=-5:2, samples=100]{exp(x)-1-1/(x+5.4)^6};
			\addplot[domain=-5:2, samples=100]{exp(x)-1-1/(x+5.4)^6-0.5};
			\addplot[domain=-5:2, samples=100]{exp(x)-1-1/(x+5.4)^6-1};
		\end{axis}
		\draw (-0.2, 2.3) node[left]{$I_\text{sat}$} -- +(1.4, 0);
		\draw (-0.2, 1.72) node[left]{$I_\text{sat}-I_\text{photo}$} -- +(1.3, 0);
	\end{tikzpicture}
	\caption{Current-voltage characteristics of a p-n junction with different levels of illumination.}\label{fig:pn_junction_iv}
\end{figure}
In \Cref{fig:pn_junction_iv} we see the current-voltage characteristics of the p-n junction under different levels of illumination.
For negative voltages, the p-n junction is operated under reverse bias.
If the reverse bias voltage exceeds the breakdown voltage the p-n junction starts to conduct.
The current before the breakdown occurs is the reverse saturation current.
For different levels of illumination, the curve is shifted downwards.
The separation between the non-illuminated (top curve) and illuminated curves represent the respective photocurrent.

The conversion rate of photons to photoelectrons depends on the type of the band gap, i.e. direct or indirect, the wavelength $\lambda$ of the photon and the temperature $T$.
Most photodiodes report a wavelength $\lambda$ dependent responsitivity $R$ which can be used to convert the radiant flux $P$ of the incident light to the generated photocurrent $I_\text{photo}$,
\begin{equation}
	I_\text{photo}=R(\lambda)P
	\label{eq:responsitivity}.
\end{equation}
For silicon-based p-n junctions, the responsitivity $R(\lambda)$ is between \SI{0.2}{\ampere\per\watt} at \SI{400}{\nano\meter} and \SI{0.6}{\ampere\per\watt} at \SI{950}{\nano\meter}.

\begin{figure}[H]
	\centering
	\begin{tikzpicture}
		\draw (1, 3.6) node {p-type};
		\draw (5, 2.2) node {n-type};
		\draw[-latex] (-0.5, -1) -- (-0.5, 3.8) node[left]{$E-e\phi$};
		\filldraw[draw=black, fill=gray] (0, 3.3) rectangle +(2, -1) +(0, -1.5) node[left]{$\mu$} -- +(2, -1.5) ++(0, -1.6) rectangle +(2, -1);
		\filldraw[draw=black, fill=gray!40] (4, 1.9) rectangle +(2, -1) +(0, -1.1) -- +(2, -1.1) node[right]{$\mu-eV$} ++(0, -1.6) rectangle +(2, -1);
		\filldraw[draw=black, fill=gray!70] (2, 3.3) -- ++(2, -1.4) -- ++(0, -1) -- ++(-2, 1.4) -- ++(0, 1);
		\filldraw[draw=black, fill=gray!70] (2, 1.7) -- ++(2, -1.4) -- ++(0, -1) -- ++(-2, 1.4) -- ++(0, 1);
		\draw[-latex] (4.2, 0.3) -- ++(0, 0.5);
		\draw (4.2, 0.5) node[right]{$E_\text{gap}-eV$};
		\foreach \x in {0, ..., 4} {
			\filldraw[fill=white] (0.2+0.4*\x, 1.5) circle (.10);
			\filldraw[fill=white] (2.2+0.4*\x, 1.3-0.275*\x) circle (.10);
			\filldraw[fill=white] (4.2+0.4*\x, 0.1) circle (.10);
			\filldraw[fill=black] (4.2+0.4*\x, 1.1) circle (.09);
			\filldraw[fill=black] (2.2+0.4*\x, 2.4-0.275*\x) circle (.09);
			\filldraw[fill=black] (0.2+0.4*\x, 2.5) circle (.09);
		};
		\filldraw[fill=white] (3.0, 1.85) circle (.10);
		\filldraw[fill=black] (3.0, 0.75) circle (.10);
		\draw[-latex] (3.0, 1.1) -- +(0, 0.4);
		\draw[-latex] (3.2, 1.85) -- +(0.4, 0);
		\draw[-latex] (2.8, 0.74) -- +(-0.4, 0);
	\end{tikzpicture}
	\caption{Energy diagram of a reverse biased p-n junction under illumination.}\label{fig:pn_junction_illumination}
\end{figure}
\Cref{fig:pn_junction_illumination} shows a p-n junction under reverse bias where a photon excites an electron-hole pair in the depletion region.
Due to the electrostatic potential, the electron is accelerated to the right side.
Analogue the hole is accelerated to the left side and in addition to the diode current, \Cref{eq:diode_current}, a photocurrent can be measured across the junction.

\subsection{Lateral photoeffect}

In the previous section, we discussed the transversal photoeffect that is usually associated with the illumination of the p-n junction.
In addition to the transversal photoeffect, the lateral photoeffect was first discovered by W. Schottky~\cite{Schottky30} in 1930 and later rediscovered in 1957 by J. Wallmark~\cite{Wallmark57}.
In the present section, we summarize important results from Ref.~\cite{Noorlag74} and Ref.~\cite{Woltring75} with focus on the tetralateral photodiode which is the most common commercially available design.
\begin{figure}[H]
	\centering
	\begin{tikzpicture}
		\filldraw[fill=gray] (0, 1.5) rectangle +(6, 0.5) node[below right]{p-type};
		\filldraw[fill=gray!40] (0, 0.5) rectangle +(6, 1) node[below right]{n-type};
		\filldraw[fill=gray!10] (0, 0) rectangle +(6, 0.5) node[below right]{resistive};
		\filldraw[fill=black] (5, 2) rectangle ++(0.5, 0.2) +(-0.25, 0) node[above]{bias};
		\draw [->, thick, decorate, decoration={snake, amplitude=3, segment length=4, post length=3}] (3, 3) node[above]{photon} -- +(0, -1);
		\filldraw[fill=black] (0.5, 0) rectangle ++(0.5, -0.2) +(-0.25, 0) node[below]{X1};
		\filldraw[fill=black] (5, 0) rectangle ++(0.5, -0.2) +(-0.25, 0) node[below]{X2};
	\end{tikzpicture}
	\caption{Cross section of a lateral photodiode.}\label{fig:lateral_photodiode_cross_section}
\end{figure}
\Cref{fig:lateral_photodiode_cross_section} depicts the cross-section of a lateral photodiode with a p-type semiconductor as the top, an n-type semiconductor as the middle layer and a resistive material as the bottom layer.
An electric contact embedded into the top layer can be used as a common cathode.
The common cathode can be connected to the ground or a positive voltage for reverse bias operation.
In contrast to the transversal photodiode, the lateral photodiode has two anode contacts positioned at the opposite sites embedded into the resistive layer.
The photocurrent measured at each of the anode contacts follows an almost linear relationship with the center-of-mass of the incident light spot.
Therefore the lateral photodiode can be used to measure the spatial coordinate of an incident light spot.

The dynamics of the lateral photodiode are guided by the Lucovsky~\cite{Lucovsky60} equation,
\begin{equation}
	\nabla^2V=\frac{\rho}{w}J_s\left(e^{eV/k_BT}-1\right)-\frac{\rho_d}{w}J_p\label{eq:lucovsky_exact},
\end{equation}
wherein $V$ is the diode voltage, $\rho$ is the resistance per unit length of the resistive layer, $J_s$ is the reverse-bias saturation current and $J_p$ is the photocurrent generated due photon induced electron-hole excitation.
\Cref{eq:lucovsky_exact} can be obtained by combination of the current density continuity equation with Ohm's law and the Schottky equation, \Cref{eq:diode_current}.

According to Ref.~\cite{Woltring75}, operation of the lateral in fully reverse-bias has the following benefits:
\begin{enumerate}
	\item Reduced signal loss.
	\item Improved response speed and resolution.
	\item Improved linearity of the position.
	\item Reduced temperature dependence.
\end{enumerate}
In electronic engineering literature, e.g. Ref.~\cite[p.~258]{Jung05}, one is sometimes discouraged from operating a photodiode under reverse-bias for highest sensitivity as the reverse-bias increased the diode leakage (dark) current.
We believe that as long as the dark current is significantly smaller than the typical photocurrent, the photodiode should always be operated in reverse-bias mode as recommended Ref.~\cite{Noorlag74,Woltring75,Wang89,Hobbs11}.

Assuming a fully reverse-biased lateral photodiode, we have $eV/k_BT\ll1$ and \Cref{eq:lucovsky_exact} simplifies to a linear second order differential (Poisson) equation,
\begin{equation}
	\nabla^2V\approx-\frac{\rho}{w}\left(J_s+J_p\right)
	\label{eq:lucovsky_reverse_bias},
\end{equation}
which can be solved using variable separation and a product Ansatz.
The solution of \Cref{eq:lucovsky_reverse_bias} depends on the imposed boundary conditions.
The Dirichlet boundary condition, $V=0$, should be used if an electrical contact terminates the semiconductor, otherwise, the Neumann boundary condition, $\pdv{V}{n}=0$, should be assumed.
\begin{figure}[H]
	\centering
	\begin{tikzpicture}
		\filldraw[fill=white] (0, 0) rectangle +(3, 3);
		\filldraw[fill=white] (4, 0) rectangle +(3, 3);
		\filldraw[fill=white] (8, 0) rectangle +(3, 3);
		\filldraw (1.5, 0.2) circle (.1);
		\filldraw (1.5, 2.8) circle (.1);
		\filldraw (0.2, 1.5) circle (.1);
		\filldraw (2.8, 1.5) circle (.1);
		\filldraw (4.4, 0.1) rectangle (6.6, 0.3);
		\filldraw (4.4, 2.7) rectangle (6.6, 2.9);
		\filldraw[fill=black!50] (4.1, 0.4) rectangle (4.3, 2.6);
		\filldraw[fill=black!50] (6.7, 0.4) rectangle (6.9, 2.6);
		\filldraw (8.4, 0.1) rectangle (10.6, 0.3);
		\filldraw (8.4, 2.7) rectangle (10.6, 2.9);
		\filldraw (8.1, 0.4) rectangle (8.3, 2.6);
		\filldraw (10.7, 0.4) rectangle (10.9, 2.6);
		\draw (1.5, 3.1) node[above]{Wallmark};
		\draw (5.5, 3.1) node[above]{Duolateral};
		\draw (9.5, 3.1) node[above]{Tetralateral};
	\end{tikzpicture}
	\caption{Contact configurations of a lateral photodiode.}\label{fig:lateral_photodiode_contacts}
\end{figure}
In \Cref{fig:lateral_photodiode_contacts} we present three different contact configurations.
The left contact configuration was used by Wallmark~\cite{Wallmark57} and comprises four small electronic contacts.
Assuming that the contact size is small compared to the surface of the photodiode, the von Neumann boundary condition have to be used.
The middle contact configuration receives great attention from Noorlag~\cite{Noorlag74}.
On two opposite sides of the photodiode an electric contact terminates the boundary while the remaining sides are left empty.
For two-dimensional position detection, one can create two electric contacts at another layer.
Mathematically we can express this configuration as combination of Neumann and Dirichlet boundary conditions.
Finally, the tetralateral configuration where each side on the same layer is terminated by electric contacts can be modelled by Dirichlet boundary conditions on all sides.
For a rectangular tetralateral photodiode of width $l$, the explicit boundary conditions are,
\begin{align}
	V(0, y)=V(l,y)=0, && V(x,0)=V(x,l)=0.
\end{align}
Together with the initial condition that a focused light spot hits the photodiode at $(x^*,y^*)$,
\begin{equation}
	V_p(x,y, t=0)=I_p\frac{\rho}{w}\delta(x-x^*)\delta(y-y^*)
	\label{eq:lucovsky_initial},
\end{equation}
the general solution of the Lucovsky equation, \Cref{eq:lucovsky_reverse_bias}, for the tetralateral configuration reads,
\begin{equation}
	V^*_p(x,y)=I_p\frac{\rho}{w}\sum_{n\in\mathbb{Z}}\sum_{m\in\mathbb{Z}}\frac{\sin(m\pi x/l)\sin(m\pi x^*/l)\sin(n\pi y/l)\sin(n\pi y^*/l)}{(m^2+n^2)\pi^2}
	\label{eq:lucovsky_solution}.
\end{equation}
The current that flows through the $x1$ contact is given by,
\begin{equation}
	I_{x1}(x^*,y^*)=\frac{w}{\rho}\int_0^l\dd{y}\eval{\pdv{V}{x}}_{x=0},
\end{equation}
respective,
\begin{equation}
	I_{x1}(x^*,y^*)=\frac{2}{\pi}I_p\sum_{n\in\mathbb{Z}}\frac{\sin[(2n-1)\pi y^*/l]}{2n-1}\frac{\sinh[\abs{2n-1}\pi(1-x^*/l)]}{\sinh(\abs{2n-1}\pi)}
	\label{eq:lucovsky_current}.
\end{equation}
The solution does not disclose the linear relationship between anode current $I_{x1}$ and the incident spot light coordinate $x^*$.
Ref.~\cite[Fig.~7]{Woltring75} renders the non-linear distortion close to the boundaries as described by \Cref{eq:lucovsky_current}.
In order to show analytically that there is an almost linear relationship between $I_{x1}$ and $x^*$, we fix $y^*=l/2$, numerically evaluate the dominant terms and Taylor expand the terms to linear order,
\begin{align}
	I_{x1}(x^*,l/2)
	&=\frac{2}{\pi}I_p\sum_{n\in\mathbb{Z}}\frac{(-1)^{n+1}}{2n-1}\frac{\sinh(\abs{2n-1}\pi(1-x^*/l))}{\sinh(\abs{2n-1}\pi)}\\
	&\approx I_p\left\{0.25-0.41731\left(\frac{x}{2l}-1\right)\right\}+\mathcal{O}\left(\left(\frac{x^*}{l}-\frac{1}{2}\right)^2\right).
\end{align}
Using the difference between two opposite contacts and normalizing for the total photocurrent, we find,
\begin{equation}
	\frac{I_{x2}(x^*,l/2)-I_{x1}(x^*,l/2)}{I_{x1}(x^*,l/2)+I_{x2}(x^*,l/2)}
	\propto\frac{x}{l},
\end{equation}
which indeed is linear in $x$.

According to Ref.~\cite[p.~41]{Noorlag74}, the tetralateral photodiode has benefits in manufacturing, although its linearity is below the duallateral photodiode, but still better than the Wallmark type, see Ref.~\cite{Woltring75}.
Recent contact configurations have improved upon the tetralateral design in order to improve the linearity.
For example, the commercially availble pin-cushion tetralateral photodiode, discussed in Ref.~\cite{Doke87,Wang89}, shows good linearity over a large area.
The center-of-mass of an incident light spot at $(x^*,y^*)$ can be recovered from the anode currents via,
\begin{align}
	\frac{\left(I_{x2}+I_{y1}\right)-\left(I_{x1}+I_{y2}\right)}{I_{x1}+I_{x2}+I_{y1}+I_{y2}}=\frac{2x^*}{l} &&
	\frac{\left(I_{x2}+I_{y2}\right)-\left(I_{x1}+I_{y1}\right)}{I_{x1}+I_{x2}+I_{y1}+I_{y2}}=\frac{2y^*}{l}	.
\end{align}
The datasheet~\cite{HamamatsuS5990} of the \gls{s5990}, a pin-cushion tetralateral photodiode, discloses the position detectability of a light spot of size \SI{0.2}{\milli\meter} over a scan interval of \SI{0.4}{\milli\meter} which does not show any non-linear distortion.

\subsection{Equivalent circuit}

In the previous section, we described the physics behind the lateral photodiode.
In the current section, we want to ignore microscopic details and concentrate on the electrical properties of real tetralateral photodiodes.

In \Cref{fig:tetralateral_photodiode_equivalent} the equivalent circuit of a tetralateral photodiode is depicted.
The tetralateral photodiode has four anode connections X1, X2, Y1, and Y2 which are connected to the junction via position-dependent resistances $R_1$, $R_2$, $R_3$, and $R_4$.
The actual junction is equivalent to two current sources $I_p,I_d$, a resistor $R_d$, and a capacitor $C_d$ in parallel.
The first current source $I_p$ represents the generated photocurrent with typical values between \si{\micro\ampere} and \si{\milli\ampere}.
The second current source $I_d$ represents the generated leakage or dark current with typical values between \si{\pico\ampere} and \si{\nano\ampere}.
\begin{figure}[H]
	\centering
	\begin{circuitikz}
		\draw (-3, -2) to[current source, l=$I_p$] ++(0, 4);
		\draw (-1, -2) node[circ]{} to[current source, l=$I_d$] ++(0, 4) node[circ]{};
		\draw (1, -2) node[circ]{} to[resistor, l=$R_d$] ++(0, 4) node[circ]{};
		\draw (3, -2) to[capacitor, l=$C_d$] ++(0, 4);
		\draw (-3, -2) -- ++(6, 0);
		\draw (-3, 2) -- ++(6, 0);
		\draw (0, -2) -- ++(0, -1) node[ocirc, label=$V_b$, rotate=180]{};
		\draw (0, 2) -- ++(0, 3) node(node)[circ]{};
		\draw (node) to[resistor, label=$R_1$] ++(2, 2) node[ocirc, label=Y1, rotate=-10]{};
		\draw (node) to[resistor, label=$R_2$] ++(-2, 2) node[ocirc, label=X1, rotate=10]{};
		\draw (node) to[resistor, label=$R_3$] ++(2, -2) node[ocirc, label=X2, rotate=-150]{};
		\draw (node) to[resistor, label=$R_4$] ++(-2, -2) node[ocirc, label=Y2, rotate=150]{};
	\end{circuitikz}
	\caption{Equivalent circuit of a tetralateral photodiode.}\label{fig:tetralateral_photodiode_equivalent}
\end{figure}
The resistance $R_d$ is referred to as interelectrode resistance and is about \SI{10}{\kilo\ohm}.
The capacitance $C_d$ is also referred to as terminal capacitance and is about \SI{150}{\pico\farad}.
Resistance $R_d$ and capacitance $C_d$ form an RC pole which frequency is given by,
\begin{equation}
	f_d=\frac{1}{2\pi R_dC_d}.
\end{equation}
For $R_d=\SI{10}{\kilo\ohm}$ and $C_d=\SI{100}{\pico\farad}$ the cut-off frequency $f_d$ of the pole is about \SI{1}{\mega\hertz}, representing the intrinsic bandwidth limit of the detector.

\subsection{Signal-to-noise ratio}

% TODO: check out Radeka1974 and Narayanan1997 for more details
% TODO: estimate non-linear errors
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

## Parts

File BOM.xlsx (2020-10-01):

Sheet: Summary
Value | Footprint | Context | Requirements | Quantity Detector | Quantity Arithmetic | Quantity Total | In Stock | Part number | Mouser | Distrelec | RS-Components | Digikey | Comment
100n | C_0603_1608Metric | Decoupling of IC from the voltage supply |  | 6 | 8 | 14 | Yes
18p | C_0603_1608Metric | Feedback capacitance of transimpedance amplifiers | Ultra-low tolerance | 4 |  | 4 | No | CC0603JRRNP09BN180 | https://www.mouser.de/ProductDetail/AVX/06035A180CAT2A?qs=sGAEpiMZZMs0AnBnWHyRQE2IRmxFPR1eBblTn5R3T4Q%3D | Not available | Not available | https://www.digikey.com/products/en?keywords=06035A180CAT2A
1u | C_0603_1608Metric | Voltage regulators / reference |  | 3 |  | 3 | Yes
10n | C_0603_1608Metric | Detector voltage regulator |  | 2 |  | 2 | Yes
22u | C_1210_3225Metric | Voltage regulators / reference |  | 3 | 2 | 5 | Low | TMK316BBJ226ML-T
10u | C_1210_3225Metric | Voltage regulators / reference |  | 1 | 2 | 3 | No | CC1210ZKY5VGBB106
5p | C_0603_1608Metric | Feedback capacitance of arithmetic amplifiers | High-precision |  | 6 | 6 | Low | CBR06C509A5GAC | https://www.mouser.de/ProductDetail/KEMET/CBR06C509A5GAC | Not available | Not available | https://www.digikey.com/product-detail/en/kemet/CBR06C509A5GAC/399-17323-1-ND/8602597
6.04k | R_0603_1608Metric | Feedback resistance of transimpedance amplifiers | High-precision | 4 |  | 4 | Yes | TNPW06036K04BEEA | https://www.mouser.de/Passive-Components/Resistors/SMD-Resistors-Chip-Resistors/_/N-7h7yu?P=1yzeg1nZ1z0srt3Z1z0srswZ1z0vnvfZ1yzmou6&Ns=Temperature%20Coefficient|0 | Not available | Not available | https://www.digikey.com/product-detail/en/te-connectivity-passive-product/RN73C1J6R04BTD/A124669CT-ND/6557714 | Mouser has better ones but they have long delivery times
100 | R_0603_1608Metric | Low-pass bias voltage reference | Temperature-stable | 1 |  | 1 | Yes
10k | R_0603_1608Metric | Feedback resistance of arithmetic amplifiers | High-precision |  | 18 | 18 | Yes
510 | R_1210_3225Metric | Power LED |  |  | 1 | 1 | No
470 | R_1210_3225Metric | Power LED |  |  | 1 | 1 | No
240 | R_1210_3225Metric | Adjustable voltage regulator | Temperature-stable |  | 2 | 2 | No
2.2k | R_1210_3225Metric | Adjustable voltage regulator | Temperature-stable |  | 2 | 2 | No | RK73H2ETTD2201F
S599x | S5990 |  |  | 1 |  | 1 | Yes
OPA2197IDx | SOIC-8_3.9x4.9mm_P1.27mm | Transimpedance amplifiers |  | 2 |  | 2 | Yes |  | https://www.mouser.de/ProductDetail/Texas-Instruments/OPA2197IDR?qs=sGAEpiMZZMutXGli8Ay4kLrcbTCwhthCZCqwegYQscU%3D | Not available | Not available | https://www.digikey.com/product-detail/en/texas-instruments/OPA2197ID/296-44779-5-ND/6198691
REF5010ID | SOIC-8_3.9x4.9mm_P1.27mm | Reverse bias voltage reference |  | 1 |  | 1 | Yes |  | https://www.mouser.de/ProductDetail/Texas-Instruments/REF5010ID | Not available | Not available | https://www.digikey.com/products/en/integrated-circuits-ics/pmic-voltage-reference/693?k=ref5010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 | Only Digikey has stocked
LT1761-5 | TSOT-23-5 | Voltage regulator detector |  | 1 |  | 1 | Yes
LT1964-5 | TSOT-23-5 | Voltage regulator detector |  | 1 |  | 1 | Yes
Conn_01x05_Male | PinSocket_1x05_P2.54mm_Vertical |  |  | 2 |  | 2 | Yes
1N4148 | D_SOD-123 | Voltage regulator arithmetic |  |  | 4 | 4 | Yes
LED | LED_0603_1608Metric | Power LED |  |  | 2 | 2 | Yes
OPA197IDx | SOIC-8_3.9x4.9mm_P1.27mm | Arithmetic operational amplifier |  |  | 3 | 3 | Yes |  | https://www.mouser.de/ProductDetail/Texas-Instruments/OPA197IDR | Not available | https://de.rs-online.com/web/p/operationsverstarker/1977408/
LM317EMP/NOPB | SOT-223-3_TabPin2 | Voltage regulator arithmetic |  |  | 1 | 1 | Yes |  | https://www.mouser.de/ProductDetail/Texas-Instruments/LM317EMPX-NOPB | https://www.distrelec.de/en/linear-voltage-regulator-25-37-sot-223-lm317-texas-instruments-lm317empx-nopb/p/30019387?q=lm317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 | Not available | https://www.digikey.com/product-detail/en/texas-instruments/LM317EMPX-NOPB/LM317EMPX-NOPBTR-ND/367000 | Sometimes they have 1A and sometimes 1.5A output current?
LM337IMP/NOPB | SOT-223-3_TabPin2 | Voltage regulator arithmetic |  |  | 1 | 1 | Yes |  | https://www.mouser.de/ProductDetail/Texas-Instruments/LM337IMP-NOPB | https://www.distrelec.de/en/linear-voltage-regulator-37-sot-223-lm337-texas-instruments-lm337imp-nopb/p/17328875?queryFromSuggest=true | https://de.rs-online.com/web/p/spannungsregler/7614612/ | https://www.digikey.com/product-detail/en/texas-instruments/LM337IMPX-NOPB/LM337IMPX-NOPBCT-ND/3526950 | Sometimes they have 1A and sometimes 1.5A output current?
Conn_01x03_Male | FanPinHeader_1x03_P2.54mm_Vertical |  |  |  | 1 | 1 | Yes |  | https://www.mouser.de/ProductDetail/Wurth-Elektronik/61900311121?qs=sGAEpiMZZMt93J8DTi5DC03qV8ayBX0k | https://www.distrelec.de/en/pin-header-straight-poles-wuerth-elektronik-61900311121/p/14385812?queryFromSuggest=true | https://de.rs-online.com/web/p/leiterplatten-header/8281474/ | https://www.digikey.com/products/en?keywords=61900311121
Conn_01x05_Male | PinHeader_1x05_P2.54mm_Vertical |  |  |  | 2 | 2 | Yes
Conn_Coaxial | SMA_Molex_73251-2120_EdgeMount |  |  |  | 3 | 3 | Yes
 | 1x03 PinHeader Steckverbinder Female

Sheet: Detector
 | References | Value | Footprint | Quantity | Stocked
1 | C1, C2, C12, C13, C14, C15 | 100n | C_0603_1608Metric | 6 | Yes
2 | C16, C17, C18, C19 | 18p | C_0603_1608Metric | 4 | Yes
3 | C3, C4, C5 | 1u | C_0603_1608Metric | 3 | Yes
4 | C6, C7 | 10n | C_0603_1608Metric | 2 | Yes
5 | C8, C9, C11 | 22u | C_1210_3225Metric | 3 | Yes
6 | C10 | 10u | C_1210_3225Metric | 1 | Yes
7 | R4, R5, R6, R7 | 6.04k | R_0603_1608Metric | 4 | Yes
8 | R1 | 100 | R_0603_1608Metric | 1 | Yes
9 | D2 | S599x | S5990 | 1 | Yes
10 | U4, U5 | OPA2197xD | SOIC-8_3.9x4.9mm_P1.27mm | 2 | Yes
11 | U3 | REF5010ID | SOIC-8_3.9x4.9mm_P1.27mm | 1 | Yes
12 | U1 | LT1761-5 | TSOT-23-5 | 1 | Yes
13 | U2 | LT1964-5 | TSOT-23-5 | 1 | Yes
14 | G*** | LOGO | mpq_lmu_logo | 1
15 | J1, J2 | Conn_01x05_Male | PinSocket_1x05_P2.54mm_Vertical | 2 | Yes

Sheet: Arithmetic
 | References | Value | Footprint | Quantity | Stocked
1 | C1, C2, C11, C12, C15, C16, C17, C18 | 100n | C_0603_1608Metric | 8 | Yes
2 | C7, C8, C9, C10, C13, C14 | 5p | C_0603_1608Metric | 6 | Yes
3 | C3, C4 | 10u | C_1210_3225Metric | 2 | Yes
4 | C5, C6 | 22u | C_1210_3225Metric | 2 | Yes
5 | R6, R7, R8, R9, R10, R12, R13, R14, R15, R16, R17, R18, R19, R20, R21, R22, R23, R24 | 10k | R_0603_1608Metric | 18 | Yes
6 | R5 | 510 | R_0603_1608Metric | 1 | No
7 | R11 | 470 | R_0603_1608Metric | 1 | No
8 | R1, R4 | 240 | R_1210_3225Metric | 2 | No
9 | R2, R3 | 2.2k | R_1210_3225Metric | 2 | No
10 | D1, D2, D3, D4 | 1N4148 | D_SOD-123 | 4 | No
11 | D5, D6 | LED | LED_0603_1608Metric | 2
12 | U3, U4, U5 | OPA197xD | SOIC-8_3.9x4.9mm_P1.27mm | 3 | Yes
13 | U1 | LM317 | SOT-223-3_TabPin2 | 1 | Yes
14 | U2 | LM337 | SOT-223-3_TabPin2 | 1 | Yes
15 | G*** | LOGO | mpq_lmu_logo | 1
16 | J1 | Conn_01x03_Male | FanPinHeader_1x03_P2.54mm_Vertical | 1 | Yes
17 | J2, J3 | Conn_01x05_Male | PinHeader_1x05_P2.54mm_Vertical | 2 | Yes
18 | J4, J5, J6 | Conn_Coaxial | SMA_Molex_73251-2120_EdgeMount | 3 | Yes

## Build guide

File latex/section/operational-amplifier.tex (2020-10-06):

\section{Operational amplifiers}

The photocurrents created by our detector are in the range of microampere where they are vulnerable to noise.
Using a preamplifier, we can increase the amplitude of the signal for an improved signal-to-noise ratio.
The typical photocurrent preamplifier is based on the transimpedance (current-to-voltage) amplifier design using a voltage-feedback operational amplifier.
Converting the current signal to a voltage has some benefits. First, an oscilloscope can monitor voltages but not currents.
Second, the voltage-feedback operational amplifier is more common than the current-feedback operational amplifier. As a consequence, manufacturers offer a broader product catalog, and there are mentions in the literature.
That said, current-feedback operational amplifiers are a viable solution for high-speed and high-bandwidth applications. Read Ref.~\cite[p.~110]{Jung05} for an overview of the benefits of current-feedback amplifiers, and Ref.~\cite[Ch.~9]{Carter17} for comparison with voltage-feedback amplifiers.
An embodiment of current-feedback operational amplifiers for high-accuracy applications can be found in Ref.~\cite[p.~143]{Noorlag74}.

In the following, we will always refer to the voltage-feedback operational amplifier if not noted otherwise.
Moreover, we expect the reader to be familiar with the foundations of the operational amplifier.
Well-written introductions to this topic can be found in \cite[Ch.~1]{Jung05} and \cite[Ch.~3]{Carter17}.

\subsection{Basic design}

\Cref{fig:basic_transimpedance} illustrates of a basic transimpedance amplifier design.
Ignoring imperfections of the photodiode, we can represent the photodiode as a current source.
The non-inverting input of the operational amplifier is connected to the ground.
The inverting input is coupled with the output of the operational amplifier via a feedback impedance $Z_f$.
\begin{figure}[H]
	\centering
	\includestandalone[mode=buildnew]{figure/circuit/amplifier-transimpedance-basic}
	\caption{Basic transimpedance amplifier using voltage feedback operational amplifier.}\label{fig:basic_transimpedance}
\end{figure}
The ideal operation amplifier has zero input current. Thus, in the node of the inverting input of the operational amplifier, Kirchhoff's law states that the current going through the feedback impedance has to cancel the current source $I_\text{in}$.
The current through the feedback impedance $Z_f$ can be expressed in terms of the feedback impedance $Z_f$ and the output voltage $V_\text{out}$ of the operational amplifier through the use of Ohm's law, yielding,
\begin{equation}
	V_\text{out}=-Z_fI_\text{in}
	\label{eq:transimpedance}.
\end{equation}
Given a maximum current $I_\text{in}$ and a desired maximum output voltage $V_\text{out}$, \Cref{eq:transimpedance} determines the feedback impedance.
Limitations arise for real operational amplifiers where the output voltage is limited to be below the operational amplifier's supply voltage.

Aside from photodiode applications, it is more common to find the inverting (voltage-to-voltage) operational amplifier in the literature.
Using the source transformation on the current source with a parallel impedance in the transimpedance amplifier circuit, we can recover the inverting operational amplifier circuit, thereby quickly obtain results for the inverting amplifier configuration.
\begin{figure}[H]
	\begin{subfigure}[t]{.5\textwidth}
		\centering
		\includestandalone[mode=buildnew]{figure/circuit/amplifier-transimpedance-input-impedance}
		\caption{Transimpedance amplifier.}
	\end{subfigure}
	\begin{subfigure}[t]{.5\textwidth}
		\centering
		\includestandalone[mode=buildnew]{figure/circuit/amplifier-inverting-input-impedance}
		\caption{Inverting amplifier.}
	\end{subfigure}
	\caption{Equivalence between transimpedance and inverting amplifier using source transformation.}\label{fig:equivalence_transimpedance_inverting}
\end{figure}
\Cref{fig:equivalence_transimpedance_inverting} shows the source transformation applied to transimpedance and inverting amplifier circuits.
Given a current source $I_\text{in}$ with parallel impedance $Z_\text{in}$ the equivalent voltage source has value $V_\text{in}=Z_\text{in}I_\text{in}$ with impedance $Z_\text{in}$ in series.

\subsection{Input offset voltage}

Real operational amplifiers only reduce the voltage difference between the inverting and non-inverting input to a non-zero input offset voltage.
For high-precision operational amplifiers, the input offset voltage is in the range of microvolts.
We can model the input offset voltage as a voltage source at the non-inverting input of an ideal operational amplifier in our transimpedance circuit, as can be seen from \Cref{fig:input_offset_voltage_transimpedance}.
In \Cref{fig:input_offset_voltage_transimpedance} we amended the basic transimpedance circuit of \Cref{fig:basic_transimpedance} by inserting a voltage source with the input offset voltage between the non-inverting input and ground.
\begin{figure}[H]
	\centering
	\includestandalone[mode=buildnew]{figure/circuit/amplifier-transimpedance-input-offset-voltage}
	\caption{Input offset voltage in the transimpedance amplifier.}\label{fig:input_offset_voltage_transimpedance}
\end{figure}
We adapt the inverting amplifier's picture to estimate the output offset $V_\text{out}$ caused by the input offset voltage $V_\text{offset}$.
\Cref{fig:input_offset_voltage_inverting} shows an inverting amplifier circuit with input impedance $Z_\text{in}$ and input offset voltage $V_\text{offset}$ at the non-inverting input of the operational amplifier.
According to the superposition theorem, we can replace the input voltage source with a short circuit to estimate the input offset voltage source's contribution.
\begin{figure}[H]
	\centering
	\includestandalone[mode=buildnew]{figure/circuit/amplifier-inverting-input-offset-voltage}
	\caption{Input offset voltage in the inverting amplifier.}\label{fig:input_offset_voltage_inverting}
\end{figure}
In \Cref{fig:input_offset_voltage_inverting}, we identify input and feedback impedance as a voltage divider with exchanged input and output nodes.
The respective transfer function reads,
\begin{equation}
	V_\text{out}=-\frac{R_f+R_\text{in}}{R_\text{in}}V_\text{offset}=-\left(1+\frac{R_f}{R_\text{in}}\right)V_\text{offset}
	\label{eq:input_offset_voltage}.
\end{equation}
Comparing \Cref{eq:input_offset_voltage} with \Cref{eq:transimpedance} discloses a difference in gain.
The gain of the input signal in Eq. 1 is commonly referred to as signal gain. 
The gain of a signal applied directly to the operational amplifier's inputs is referred to as noise gain.
In the case of the position-sensitive detector, the input resistance is of order \SI{10}{\kilo\ohm}.
Using a feedback resistance of $R_f=\SI{100}{\kilo\ohm}$, we find that the input offset voltage experiences a gain of 11.

One approach to compensate for the input offset voltage as described is depicted in \Cref{fig:input_offset_voltage_compensation}, see also Ref~\cite[p.~54]{Jung05}.
A potentiometer with maximum resistance Rp connects the positive and negative supply voltage.
The wiper of the potentiometer is connected with a first resistor R1 to a node.
The node is connected with a second resistor R2, and an optional bypass capacitor to ground.
Finally, the equivalent input offset voltage source connects the node with the operational amplifier's non-inverting input.
\begin{figure}[H]
	\centering
	\includestandalone[mode=buildnew]{figure/circuit/offset-compensation}
	\caption{Input offset voltage compensation using adjustable potentiometer.}\label{fig:input_offset_voltage_compensation}
\end{figure}
Let $0\leq x\geq1$ be the position of the potentiometer.
For $x=1/2$, the potentiometer's resistance is $R_p/2$ and there is no offset compensation.
For $x<1/2$, the input offset compensation is negative to compensate for a positive input offset voltage.
For $x>1/2$, the input offset compensation is positive to compensate for a negative input offset voltage.
The maximum input offset compensation is obtained for $x=0$ and $x=1$.
Using circuit analysis techniques, we obtain,
\begin{equation}
	V_c(x)=\frac{R_2(1-2x)}{R_1+R_2-R_p(1-x)x}V_\text{supply},
\end{equation}
as an analytical expression for the input offset voltage compensation measured between the node and ground.
The maximum absolute value of the compensation voltage follows to be,
\begin{equation}
	V_c(0)=V_c(1)=\pm\frac{R_2}{R_1+R_2}V_\text{supply}.
\end{equation}
Given a maximum input offset voltage of \SI{100}{\micro\volt} and a supply voltage of \SI{15}{\volt}, we find approximate resistor values $R_1=\SI{3}{\mega\ohm}$ and $R_2=\SI{2}{\ohm}$.
The resistor value of the potentiometer $R_p$ should be sufficiently large to limit the current.
For example, a potentiometer resistance of $R_p=\SI{15}{\kilo\ohm}$ would limit the current to \SI{2}{\milli\ampere} with a heat dissipation of \SI{60}{\milli\watt}.
In practice, one should aim for a slightly higher maximum compensation voltage to handle resistor mismatches.

That said, there are some practical arguments against the use of the described input offset voltage compensation.
The first argument is that the low resistance of $R_2$ acts as a dominant source for thermal current noise density of about \SI{100}{\pico\ampere\per\sqrt\hertz}.
As this current noise contributes to the transimpedance amplifier's input, it gets amplified by the feedback impedance $Z_f$, yielding up to \SI{110}{\micro\volt\per\sqrt\hertz} in voltage noise density, which --- depending on the bandwidth --- surpasses the actual input offset voltage to compensate.
The second argument is that high-precision potentiometers with large dynamic range get very large and complicated to accommodate on a printed circuit board.

\subsection{Input bias current}

In addition to the input offset voltage $V_\text{offset}$, there is a second effect that causes an offset in the output voltage $V_\text{out}$.
This second effect stems from the small amount of current drawn from the inputs of the operational amplifier.
We highlighted the input currents in \Cref{fig:input_bias_current} where they are represented by the current flows $i_+$ and $i_-$ directly pointing into the inputs of the operational amplifier in the transimpedance circuit.
\begin{figure}[H]
	\centering
	\includestandalone[mode=buildnew]{figure/circuit/amplifier-transimpedance-input-bias-current}
	\caption{Input bias current offset in the transimpedance amplifier.}\label{fig:input_bias_current}
\end{figure}
Input bias currents for high-precision operational amplifiers are in the range of picoamperes.
These small currents are usually difficult to measure and may differ between inputs.
The datasheet of the operational amplifier doesn't report the input bias current per terminal. Instead, the mean $I_\text{bias}$ and the difference between the input currents $I_\text{offset}$ are specified.
The relationship between the mean input bias current $I_\text{bias}$ and the input offset current $I_\text{offset}$ for the actual input bias currents $i_+,i_-$ is given below.
\begin{align}
	i_+=I_\text{bias}+\frac{1}{2}I_\text{offset} &&
	I_\text{offset}=i_+-i_- \\
	i_-=I_\text{bias}-\frac{1}{2}I_\text{offset} &&
	I_\text{bias}=\frac{i_++i_-}{2}
\end{align}
According to Ref.~\cite[p.~57]{Jung05} and Ref.~\cite[p.~25]{Graeme96} the effect of the input bias currents $i_+,i_-$ on the output voltage $V_\text{out}$ can be compensated with an impedance $Z_c$ at the non-inverting input of the operational amplifier.
\Cref{fig:input_bias_current_compensation} illustrates the inverting amplifier configuration with such a compensation impedance $Z_c$.
\begin{figure}[H]
	\centering
	\includestandalone[mode=buildnew]{figure/circuit/amplifier-inverting-input-current-compensation}
	\caption{Input current offset compensation.}\label{fig:input_bias_current_compensation}
\end{figure}
Following the argumentation from Ref.~\cite[p.~383]{Terrel96}, the input bias current at the inverting input of the operational amplifier $i_-$ develops a voltage of $Z_fi_-$ over the feedback impedance $Z_f$.
The input bias current at the non-inverting input $i_-$ develops the voltage $Z_ci_-$ over the compensation resistor $Z_c$.
The voltage $Z_ci_-$ propagates through the voltage divider comprising the feedback and input impedance analog to the input offset voltage.
According to the superposition theorem, both of these contributions add and yield,
\begin{equation}
	V_\text{out}=i_+Z_c\left(1+\frac{Z_f}{Z_\text{in}}\right)-i_-Z_f
	\label{eq:input_bias_current},
\end{equation}
at the output voltage.
If $i_+\approx i_-$ we can choose,
\begin{equation}
	Z_c=\frac{Z_\text{in}}{Z_\text{in}+Z_f},
\end{equation}
 to compensate for the output voltage offset caused by the input bias currents.
The condition $i_+\approx i_-$ is usually satisfied if the input offset current $I_\text{offset}$ reported in the datasheet is less than the mean input bias current $I_\text{bias}$.
High-precision operational amplifiers usually have compensated bias currents that do not satisfy this condition.
In this case, there is no generic formula for the value of the compensation impedance $Z_c$ in terms of input and feedback impedance, and one needs to perform impedance matching on a per-device basis.
One should keep in mind that high-precision operational amplifiers have input bias currents in the range of \si{\pico\ampere}.
Using \Cref{eq:input_bias_current}, one should first check if the output voltage offset due to input bias currents is even worth compensating compared to other offset and noise contributions.

\subsection{Stability and bandwidth}\label{sec:opamp_stability_bandwidth}

The outputs of the transimpedance and inverting amplifier designs have a phase shift of \SI{180}{\degree}.
If an additional phase shift of \SI{180}{\degree} accumulates because of the inherent bandwidth limitations of the operational amplifier and the gain is equal or greater than unity, the conditions for oscillations are met, and the amplifier will become unstable, see Ref.~\cite[p.~395]{Terrel96}.
By artificially limiting the bandwidth with an additional frequency pole, we can flatten out the frequency response at high frequencies, and thereby stabilize the amplifier, see Ref.~\cite[p.~184]{Kay12}.

\Cref{fig:bode_gain} shows a Bode plot of the open-loop (black) and noise gain (red) of an operational amplifier.
The noise gain separates into a compensated (solid) and uncompensated (dotted) branch.
\begin{figure}[H]
	\centering
	\includestandalone[mode=buildnew]{figure/plot/bode-operational-amplifier}
	\caption{Bode plot of the open-loop and closed-loop gain of the amplifier.}\label{fig:bode_gain}
\end{figure}
With the uncompensated branch, we would observe instability due to oscillations.
Through the addition of a feedback capacitor, we obtain the compensated branch.
According to Ref.~\cite[p.~113]{Jung05}, Ref.~\cite[p.~693]{Hobbs11} and Ref.~\cite[Ch.~3]{Graeme96} the value for the feedback capacitance is given by,
\begin{equation}
	C_f\geq\sqrt{\frac{C_\text{in}}{2\pi R_f f_u}}
	\label{eq:feedback_capacitance_approximation},
\end{equation}
wherein $R_f$ denotes the feedback resistance and $f_u$ the unity-gain-bandwidth of the operational amplifier.
The capacitance should be larger to ensure the design margin.
The unity-gain-bandwidth of the operational amplifier denotes the frequency where the open-loop gain equals unity. In the datasheet of the operational amplifier, said frequency is reported as \gls{gbp}.
$C_\text{in}$ in \Cref{eq:feedback_capacitance_approximation} represents the sum of the amplifier circuit's input capacities and the capacitance of the signal source.
According to Ref.~\cite[p.~185]{Carter17} a more exact formula for the feedback capacitance is given by,
\begin{align}
	C_f\geq\frac{C_\text{aux}}{2}\left(1+\sqrt{1+\frac{4C_\text{in}}{C_\text{aux}}}\right) &&
	C_\text{aux}=\frac{1}{2\pi R_f f_u}
	\label{eq:feedback_capacitance_exact},
\end{align}
which is also valid if not $C_\text{in}\gg C_f$.

\Cref{fig:capacitive_transimpedance} illustrates the transimpedance amplifier with capacitive elements.
Parallel to the current source $I_\text{in}$, we find the input capacitance $C_\text{in}$ comprising source capacitance and operational amplifier capacitance.
Parallel to the feedback resistance $R_f$ we find the feedback capacitance $C_f$ with value given in \Cref{eq:feedback_capacitance_exact} or \Cref{eq:feedback_capacitance_approximation}.
\begin{figure}[H]
	\centering
	\includestandalone[mode=buildnew]{figure/circuit/amplifier-transimpedance-input-capacitance}
	\caption{Transimpedance amplifier with capacitive elements.}\label{fig:capacitive_transimpedance}
\end{figure}
% TODO: why use noise gain
% TODO: definition open-loop gain, closed-loop gain
% TODO: why is rate of closure important for stability (relation with phase margin?)

As noted earlier, the bandwidth reduces with an additional feedback capacitor.
The new bandwidth is now given by the RC pole formed by the feedback impedance
\begin{equation}
	BW=\frac{1}{2\pi R_fC_f}.
\end{equation}
Given a unity-gain-bandwidth of the operational amplifier of $f_u=\SI{10}{\mega\hertz}$ and a feedback resistance of $R_f=\SI{100}{\kilo\ohm}$ \Cref{eq:feedback_capacitance_approximation} yields a minimum feedback capacitance of $C_f=\SI{4}{\pico\farad}$.
Together with $R_f$, the feedback capacitance limits the bandwidth to about \SI{400}{\kilo\hertz}.

% \subsection{Signal-to-noise ratio}

% TODO: (Jung, p. 80)
% TODO: thermal noise from resistor
% TODO: equivalent noise from operational amplifier

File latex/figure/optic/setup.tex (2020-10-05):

\documentclass[tikz]{standalone}

\begin{document}
	\begin{tikzpicture}[scale=3]
		\pgfmathsetmacro{\lensRadius}{0.6}
		\pgfmathsetmacro{\lensHeight}{.3}
	  	\pgfmathsetmacro{\startAngle}{asin(\lensHeight/\lensRadius)}
	  	\draw[color=green] (0.5, 0) -- ++(2, 0) node(A){} -- ++(0, 1) node(B){} -- ++(-2.5, -0.2);
		\node[draw, fill=white] at (0.4, 0) {Laser};
		\draw[thick] (2.32, -0.18) -- ++(45:0.5);
		\draw[thick] (2.32, 1.2) -- ++(-45:0.5);
		\draw [fill=blue!15]  (0.9,\lensHeight+0.85)
  arc[start angle=180-\startAngle,delta angle=2*\startAngle,radius=\lensRadius]
  arc[start angle=-\startAngle,delta angle=2*\startAngle,radius=\lensRadius]
   -- cycle;
	   \draw[draw=black, fill=white] (-.1, 0.6) rectangle ++(0.2,0.4);
	   \node at (0, 0.48) {Detector};
	   \node at (0.9, 0.48) {Lens};
	   \node at (0, 0.48) {Detector};
	   \node at (2.6, -0.3) {Mirror (M1)};
	   \node at (2.6, +1.3) {Mirror (M2)};
	\end{tikzpicture}
\end{document}

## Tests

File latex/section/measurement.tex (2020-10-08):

\section{Measurement}

In the present section, we will perform some measurements with the \gls{psd}.
In particular, we want to determine the spatial resolution and discuss the noise characteristics.

\subsection{Electrical setup}

\Cref{tab:equipment} lists the equipment required for the electrical setup.
The electric devices are connected as follows.
The \gls{psd} is connected with the power supply through the LEMO4 cable.
The DIFFX, DIFFY, and SUM output voltages of the \gls{psd} are conencted to the oscilloscope's first three input channels.
It is essential to use shielded cables to avoid receiving \SI{50}{\hertz} noise from surroudning switching power supplies.

\begin{table}[htb]
  \centering
  \begin{tabular}{ccl}
    \toprule
      Device & Amount \\
    \midrule
      \gls{psd} & 1\\
      Oscilloscope & 1\\
      \SI{\pm15}{\volt} voltage supply & 1\\
      Shielded LEMO4 cable & 1\\
      Shielded \acrshort{sma} cable & 3\\
      \acrshort{sma} to \acrshort{bnc} adapters & 3\\
    \bottomrule
  \end{tabular}
  \captionsetup{width=.8\textwidth}
  \caption{Electrical equipment required to operate the \gls{psd}}\label{tab:equipment}
\end{table}

You can configure the oscilloscope to show the first two input channels in X-Y mode.
In X-Y mode, the signal on the coordinate grid corresponds to the position of the incident light spot.
Suppose your light source shows strong intensity fluctuations.
In that case, you can use the oscilloscope's arithmetic operation to divide the DIFFX and DIFFY signals by the SUM signal.

\subsection{Optical setup}

\Cref{fig:optical_setup} shows an optical setup for spatial resolution measurements.
The arrangement comprises a laser source, two mirrors, a lens with focal length $f=\SI{50}{\milli\meter}$ positioned in \SI{11}{\centi\meter} distance from the \gls{psd}.
Using two mirrors instead of one allows more freedom in positioning the other optics.
The lens focuses the laser beam onto the sensitive area of the \gls{psd}.
\begin{figure}[htb]
	\centering
	\includestandalone[mode=buildnew]{figure/optic/setup}
	\caption{Optical setup for testing}\label{fig:optical_setup}
\end{figure}
We measured an optical power of $P=\SI{1}{\milli\watt}$ for the red laser at $\lambda=\SI{700}{\nano\meter}$ with the optical power meter.

\subsection{Grid scan}

\begin{figure}[H]
	\centering
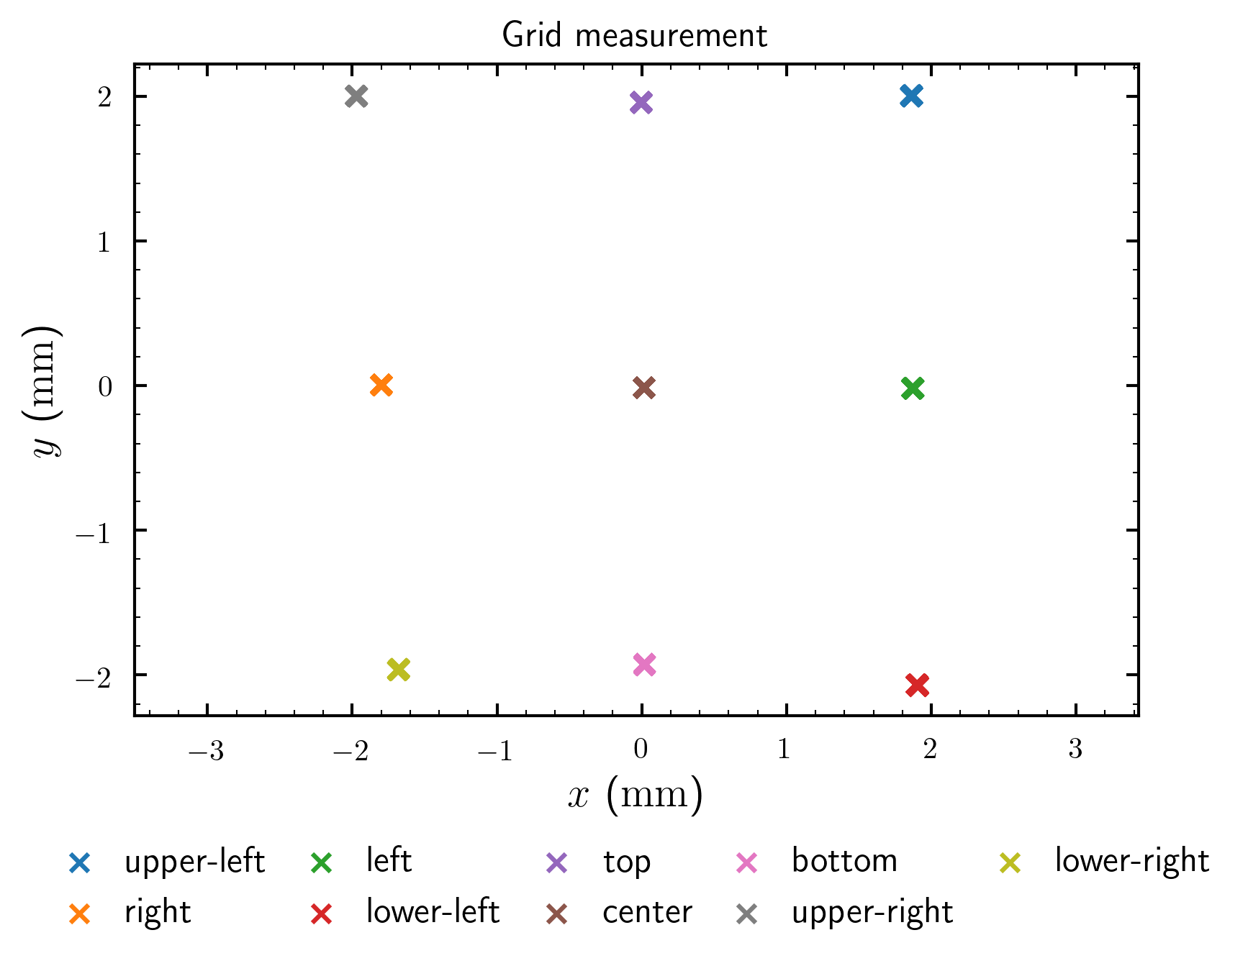
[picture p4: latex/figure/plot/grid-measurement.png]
	
	\caption{Spatial scan over $3\times 3$ grid by adjusting the mirrors.}\label{fig:grid_scan}
\end{figure}
\Cref{fig:grid_scan} shows the positions of a 3 x 3 grid scan.
We adjusted mirror M2 in the optical setup shown in \cref{fig:optical_setup} and captured a trace with the oscilloscope.
In the post-processing, we converted the captured voltages to positions.
The datasheet of the S5990 position-sensitive photodiode gives a conversion formula for the photocurrents
\begin{align}
	\frac{(I_2+I_3)-(I_1+I_4)}{I_1+I_2+I_3+I_4}=\frac{2x}{L},
	&&
	\frac{(I_2+I_4)-(I_1+I_3)}{I_1+I_2+I_3+I_4}=\frac{2y}{L}
	\label{eq:position_conversion_photocurrent},
\end{align}
wherein $L$ is the length of the photodiode's quadratic sensitive area.
In our case, we have the smaller S5991-01 photodiode where $L = \SI{4}{\milli\meter}$.
In terms of the output voltage signals of the \gls{psd}, the positions are then given by
\begin{align}
	x=\frac{L}{2}\frac{\text{DIFFX}}{\text{SUM}}\ \si{\milli\meter}, &&
	y=\frac{L}{2}\frac{\text{DIFFY}}{\text{SUM}}\ \si{\milli\meter}.
	\label{eq:position_conversion_voltages}
\end{align}

\subsection{Resolution}

\begin{figure}[htb]
	\centering
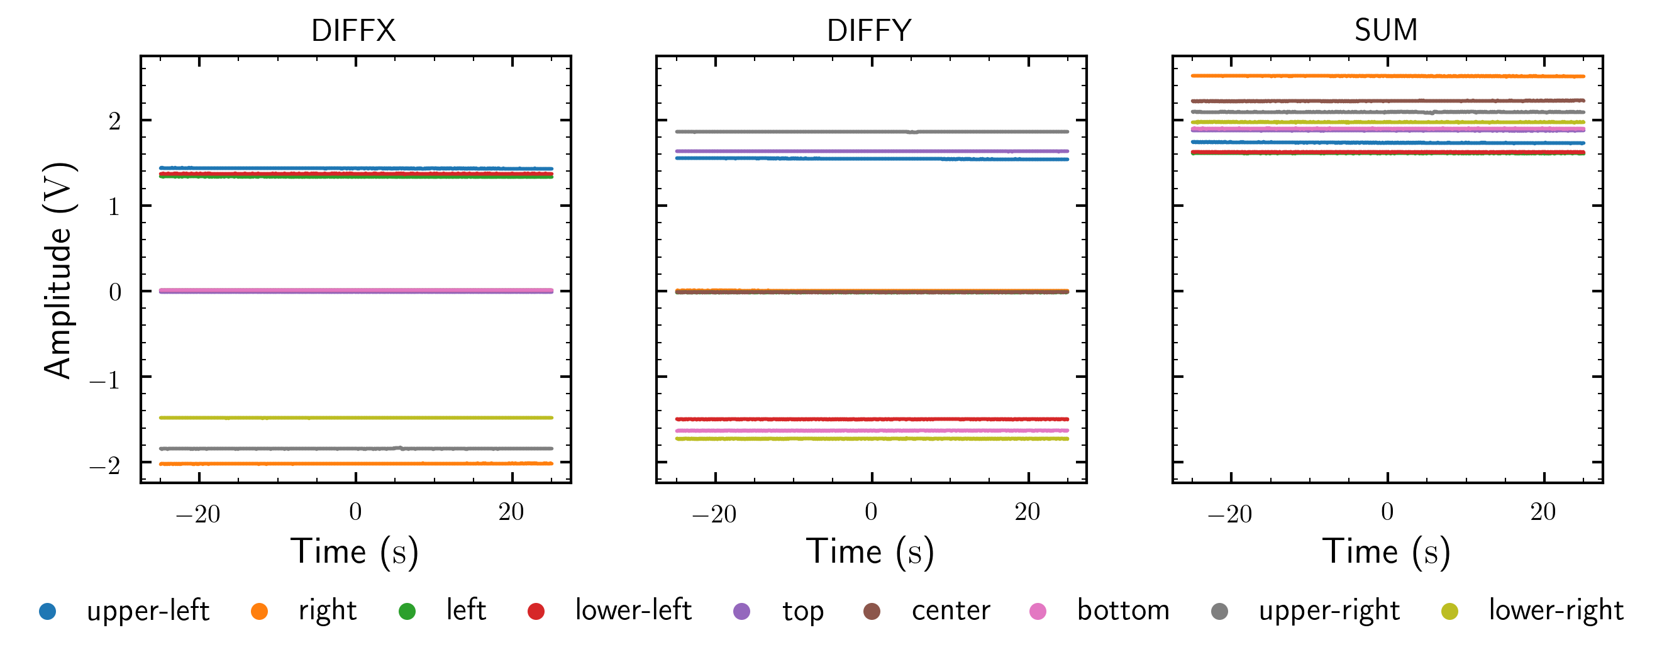
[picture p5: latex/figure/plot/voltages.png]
	
	\caption{Timeseries of the voltage signals captured during the grid scan.}\label{fig:grid_scan_voltages}
\end{figure}
\Cref{fig:grid_scan_voltages} shows the voltage signals for the grid scan measurement.
The change of the SUM signal for the different measurements indicates a change in the total intensity of the detected light.
We note that the difference signals span a voltage range from \SI{-2}{\volt} to \SI{+2}{\volt}.

\begin{figure}[htb]
	\centering
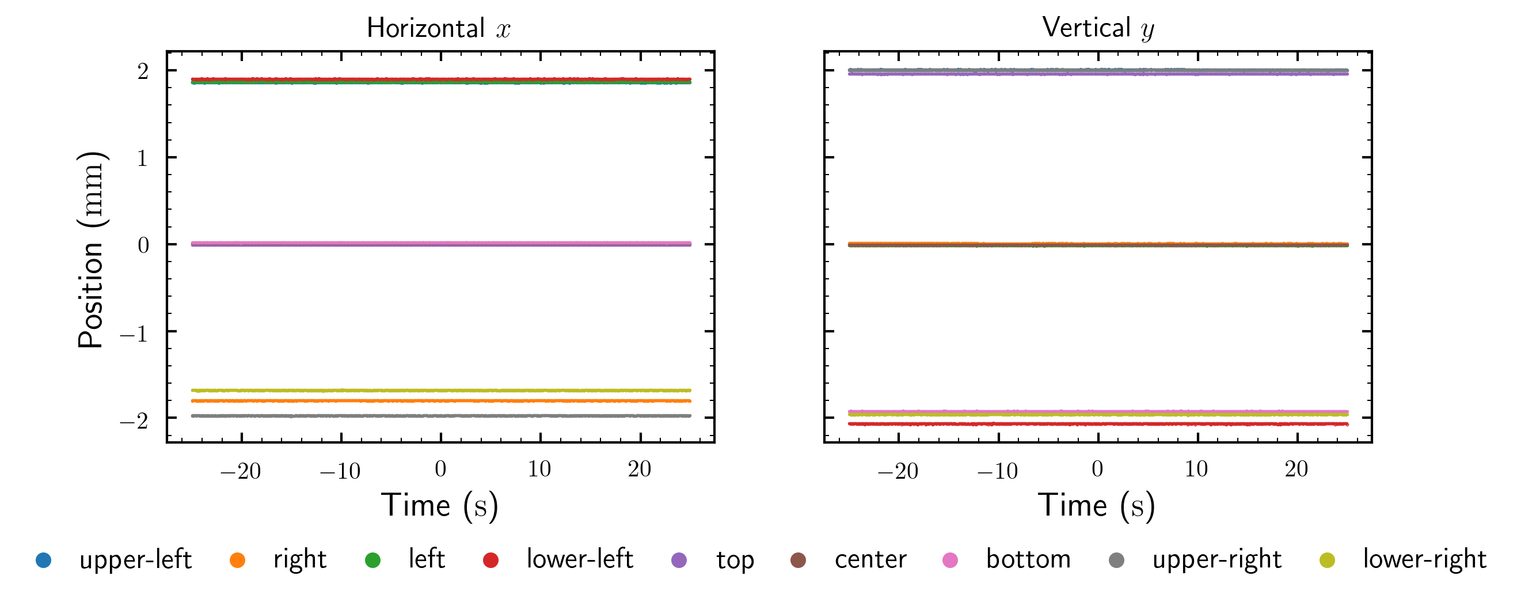
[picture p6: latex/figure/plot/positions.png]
	
	\caption{Voltage signals of the grid scan converted to positions.}\label{fig:grid_scan_positions}
\end{figure}
\Cref{fig:grid_scan_positions} shows the positions obtained from the voltages signals after using \cref{eq:position_conversion_photocurrent}.
Horizontal and vertical axis span an area of close to \SI{4}{\milli\meter} in agreement with the specified length of the sensitive area of the S5991-01.
We explain small deviations by the fact that we cannot precisely control the mirror adjustments.

\Cref{tab:grid_scan_position_statistics} summarizes the statistics, mean and standard deviation, of the position traces illustrated in \cref{fig:grid_scan_positions}.
For different grid positions, we find different positional uncertainty.
The highest resolution with about \SI{1}{\micro\meter} is obtained close to the center.
This is in agreement with our theoretical discussion of the position-sensitive photodiode designs where we claimed that non-linear effects become notable close to the border of the sensitive area.
\begin{table}[htb]
  \centering
  \begin{tabular}{lcccc}
    \toprule
      Measurement &
      $x$ (\si{\milli\meter}) &
      $\Delta x$ (\si{\micro\meter}) &
      $y$ (\si{\milli\meter}) &
      $\Delta y$ (\si{\micro\meter}) \\
    \midrule
      Center & \num{0.01} & \num{+1.08} & \num{-0.01} & \num{+1.03} \\      
      Top & \num{-0.01} & \num{+1.30} & \num{+1.96} & \num{+1.67} \\      
      Left & \num{1.87} & \num{+2.19} & \num{-0.01} & \num{+1.50} \\      
      Right & \num{-1.80} & \num{+1.38} & \num{+0.01} & \num{+1.61} \\
      Bottom & \num{0.02} & \num{+1.24} & \num{-1.92} & \num{+2.11} \\
      Upper left & \num{+1.86} & \num{+2.03} & \num{+2.01} & \num{+2.50} \\
      Upper right & \num{-1.97} & \num{+1.75} & \num{+2.00} & \num{+1.65} \\
      Lower left & \num{+1.90} & \num{+2.26} & \num{-2.07} & \num{+2.56} \\
      Lower right & \num{-1.68} & \num{+1.78} & \num{-1.96} & \num{+1.87} \\
    \bottomrule
  \end{tabular}
  \captionsetup{width=.8\textwidth}
  \caption{Position statistics of $3\times 3$ grid scan}\label{tab:grid_scan_position_statistics}
\end{table}

\subsection{Dark noise}

For completeness, we performed a measurement of the detector where the sensitive area is blocked.
\Cref{tab:dark_statistics} summarizes the statistics of the measurement.
\begin{table}[htb]
  \centering
  \begin{tabular}{lcc}
    \toprule
      Signal &
      Mean (\si{\milli\volt}) &
      Standard deviation (\si{\micro\meter}) \\
    \midrule
      DIFFX & \num{0.1} & \num{17} \\
      DIFFY & \num{0.4} & \num{17} \\
      SUM & \num{1.2} & \num{32} \\
    \bottomrule
  \end{tabular}
  \captionsetup{width=.8\textwidth}
  \caption{Signal statistics obtained without illumination}\label{tab:dark_statistics}
\end{table}
The variance of the voltage signals without illumination are much less than with illumination.
It is difficult to distinguish the electronic from the detector noise.

\subsection{Gaussian beam waist}

Finally, we want to compare the focused beam waist to the positional uncertainty of \cref{tab:grid_scan_position_statistics}.

In Gaussian beam optics, we define the Rayleigh length
\begin{equation}
	z_R=\frac{\pi w_0^2}{\lambda}
	\label{eq:rayleigh_length}.
\end{equation}
Using a white paper, a pen, and a ruler, we estimated the spot size in front of the lens in \cref{fig:optical_setup} to be less than $w_0=\SI{3}{\milli\meter}$.
For simplicity, we assume $\lambda=\SI{700}{\nano\meter}$ as the laser wavelength, and estimate the Rayleigh length to be $z_R=\SI{40}{\meter}$.

Consider a Gaussian beam with initial beam waist $w_0$ and Rayleigh length $z_R$ propagating through a thin lens with focal length $f$.
After a distance of $s$, the beam waist of the Gaussian beam has the size
\begin{equation}
	w^\prime_0=\frac{w_0}{\sqrt{(1-s/f)^2+(z_R/f)^2}}
	\label{eq:beam_waist_thin_lens}.
\end{equation}
For the optical setup given in \cref{fig:optical_setup}, $z_R=\SI{40}{\meter}$, $w_0=\SI{3}{\milli\meter}$, $s=\SI{11}{\centi\meter}$, $f=\SI{50}{\milli\meter}$, \cref{eq:beam_waist_thin_lens} yields $w^\prime_0=\SI{4}{\micro\meter}$.
A beam waist of \SI{4}{\micro\meter} is four times the estimated position uncertainty at the center of the \gls{psd}.
We conclude that it is unlikely for the position uncertainty to be related to the spot size.

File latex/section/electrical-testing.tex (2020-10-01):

\section{Electrical testing}

With the electrical testing, we want to confirm that the solder connections and components work as expected.
The most basic check is that the supply voltages are correct.
More elaborated checks concern the operational amplifiers but are out of the scope of this document.

\subsection{Arithmetic board I}

Leave the arithmetic board unpowered and measure the resistance between the supply lines through the test points TP1 (+12 V), TP2 (GND), and TP3 (-12 V).
There should be very high resistance between any of these test points.
Otherwise, there is a short.

If no short is detected, you can configure the power supply to provide a dual voltage of +- 15 V.
Alternatively, use two single voltage sources set to 15 V and connect the negative port of one of the voltage sources with the other one's positive voltage.
Confirm that the output voltages are correct with the multimeter. If possible, limit the current of the voltage sources.
You can set the current limit as low as possible and increase from there until the voltage becomes stable.
You might need to adjust the limit when connecting the voltages with the arithmetic board.

Connect the power supply with the arithmetic board but double-check the polarity.
The voltage between TP2 (GND) and TP1 (+12 V) should read around + 12 V while the voltage between TP2 (GND) and TP3 (- 12 V) should read about - 12 V.

Confirm that the supply voltages reach the op-amps.
Check the temperature of the op-amps.
If the op-amps are very hot, there is a short.
You can additionally check if the op-amps work by grounding the inverting input.
Because the op-amp's non-inverting input is connected with the ground, the op-amp output should be a virtual ground.

\subsection{Detector board}

Have the detector board unplugged and measure the resistance between GND (you can use the center pin of the headers), TP5 (+ 5V), and TP6 (-5 V). If the resistance is high, proceed. Otherwise, find the short.

Measure the voltage between the photodiode and GND's outer pins while illuminating the sensitive area of the photodiode with a laser pointer.
You should detect a small voltage.

If the preceding checks are successful, mount the detector board on the arithmetic board, and measure the detector board's supply voltages.

Finally, confirm that the voltage reference (U3) outputs 10 V and that the op-amps have the correct supply voltage.

\subsection{Arithmetic board II}

Leave the detector board mounted on the arithmetic board.
Measure the voltage at the outputs of the operational amplifiers of the arithmetic board.
For the summing amplifier (U5), we expect an increase in voltage when illuminating the photodiode with the laser pointer.
For the difference amplifiers (U3, U4), we expect the voltage to change when moving the laser pointer's focal spot on the photodiode.

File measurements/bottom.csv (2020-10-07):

x-axis | 1 | 2 | 3
second | Volt | Volt | Volt
-25.00000E+00 | +14.06E-03 | -1.62906E+00 | +1.90375E+00
-24.95000E+00 | +14.06E-03 | -1.62906E+00 | +1.90531E+00
-24.90000E+00 | +14.06E-03 | -1.62906E+00 | +1.90219E+00
-24.85000E+00 | +14.06E-03 | -1.62906E+00 | +1.90375E+00
-24.80000E+00 | +12.50E-03 | -1.62750E+00 | +1.90687E+00
-24.75000E+00 | +14.06E-03 | -1.62750E+00 | +1.90219E+00
-24.70000E+00 | +15.63E-03 | -1.62906E+00 | +1.90375E+00
-24.65000E+00 | +14.06E-03 | -1.62906E+00 | +1.90375E+00
-24.60000E+00 | +14.06E-03 | -1.62750E+00 | +1.90375E+00
-24.55000E+00 | +12.50E-03 | -1.62750E+00 | +1.90375E+00
-24.50000E+00 | +17.19E-03 | -1.62750E+00 | +1.90062E+00
-24.45000E+00 | +15.63E-03 | -1.63219E+00 | +1.90531E+00
-24.40000E+00 | +12.50E-03 | -1.62750E+00 | +1.90531E+00
-24.35000E+00 | +14.06E-03 | -1.62906E+00 | +1.90375E+00
-24.30000E+00 | +14.06E-03 | -1.62750E+00 | +1.90375E+00
-24.25000E+00 | +14.06E-03 | -1.62594E+00 | +1.90375E+00
-24.20000E+00 | +14.06E-03 | -1.62750E+00 | +1.90531E+00
-24.15000E+00 | +14.06E-03 | -1.62906E+00 | +1.90531E+00
-24.10000E+00 | +14.06E-03 | -1.62906E+00 | +1.89906E+00
-24.05000E+00 | +15.63E-03 | -1.62750E+00 | +1.90375E+00
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

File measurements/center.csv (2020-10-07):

x-axis | 1 | 2 | 3
second | Volt | Volt | Volt
-25.00000E+00 | +14.06E-03 | -10.94E-03 | +2.22344E+00
-24.95000E+00 | +14.06E-03 | -10.94E-03 | +2.22344E+00
-24.90000E+00 | +14.06E-03 | -9.38E-03 | +2.22187E+00
-24.85000E+00 | +10.94E-03 | -9.38E-03 | +2.22187E+00
-24.80000E+00 | +14.06E-03 | -10.94E-03 | +2.22344E+00
-24.75000E+00 | +12.50E-03 | -12.50E-03 | +2.22344E+00
-24.70000E+00 | +12.50E-03 | -10.94E-03 | +2.22187E+00
-24.65000E+00 | +14.06E-03 | -10.94E-03 | +2.22187E+00
-24.60000E+00 | +12.50E-03 | -10.94E-03 | +2.22187E+00
-24.55000E+00 | +14.06E-03 | -10.94E-03 | +2.22187E+00
-24.50000E+00 | +15.63E-03 | -9.38E-03 | +2.22344E+00
-24.45000E+00 | +12.50E-03 | -12.50E-03 | +2.22344E+00
-24.40000E+00 | +14.06E-03 | -9.38E-03 | +2.22344E+00
-24.35000E+00 | +15.63E-03 | -12.50E-03 | +2.22031E+00
-24.30000E+00 | +14.06E-03 | -9.38E-03 | +2.21875E+00
-24.25000E+00 | +12.50E-03 | -10.94E-03 | +2.22031E+00
-24.20000E+00 | +14.06E-03 | -10.94E-03 | +2.22187E+00
-24.15000E+00 | +14.06E-03 | -10.94E-03 | +2.22500E+00
-24.10000E+00 | +12.50E-03 | -10.94E-03 | +2.22344E+00
-24.05000E+00 | +14.06E-03 | -12.50E-03 | +2.22031E+00
-24.00000E+00 | +12.50E-03 | -10.94E-03 | +2.22344E+00
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

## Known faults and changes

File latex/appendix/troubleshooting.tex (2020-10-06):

\section{Troubleshooting}

In this section, we record phenomena and their respective origin that we found during debugging\footnote{In the following, we use the term "noise" in the generic sense of (strong) unwanted signal instead of the strict statistical sense. Of course, random noise, e.g., thermal or shot noise, will always be present.}.

\subsection{Shorts}

The most common sources for shorts we experienced originated from the soldering process.
More precisely, this means displaced components and adverse solder joints.
The best strategy to find shorts is by using a microscope and scrutinizing the solder points.
If this doesn't help, one needs to remove components step-by-step.
As we had most problems with capacitors, we recommend starting with the capacitors.

Alternative strategies for finding shorts include using an \gls{ir} camera to detect hot spots on the \gls{pcb}.
However, this won't work for shorts caused by unwanted solder.
A very advanced technique measures the voltage drop across the components to narrow down the short.
Consult your electrical engineer for details.

\subsection{\SI{50}{\hertz} noise}

\SI{50}{\hertz} noise is a characteristic of switching power supplies.
We found that unisolated banana cables connected to a laboratory power supply act as an antenna.
We highly recommend using isolated LEMO4 cables for power supply.

\subsection{Power supply noise}

When searching for noise sources, always check that the power supply provides clean voltages.
More than once did we experience defect photodiode power supplies where this was not the case.

\subsection{Unstable operational amplifiers}

If the feedback capacitance is too small, operational amplifiers can become unstable.
Unstable operational amplifiers behave as high-frequency oscillators.
For more details on operational amplifier stability consult \cref{sec:opamp_stability_bandwidth}.
One can quickly check if an operational amplifier is a source for oscillations by grounding the input pins.
Grounded input pins should yield a zero output voltage of the operational amplifier, i.e., make the oscillations vanish.

\subsection{Malfunctioning capacitors}

Broken capacitors are the most difficult to find troublemakers. 
We found one of them at the voltage regulator and another at the voltage reference.
In both cases, the supply voltage was highly unstable and oscillating.
We believe that using high-capacitance with a small casing size, e.g., 0603, increases the risk of malfunction.
For this reason, we use large casing sizes, e.g., 1210, for high-capacitance capacitors in the recent design.

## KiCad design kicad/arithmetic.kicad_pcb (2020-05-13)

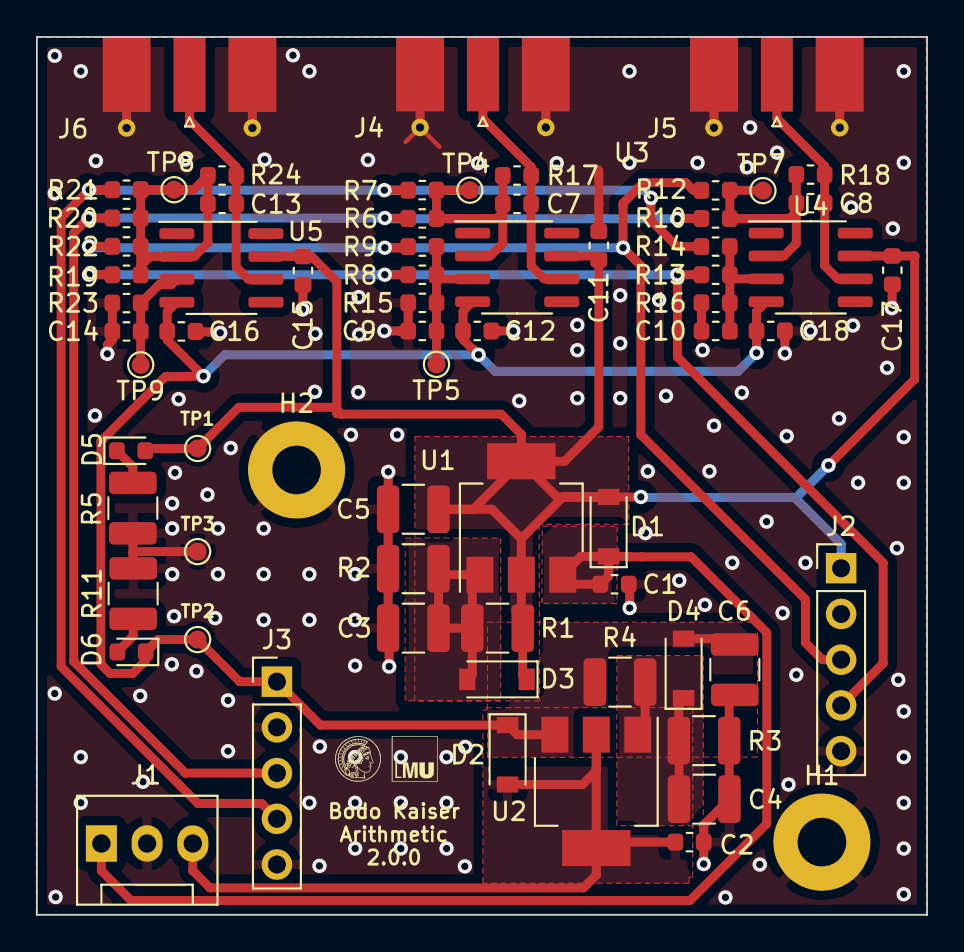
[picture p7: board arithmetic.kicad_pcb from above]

Board: 2 copper layers, 49.5 x 48.8 mm, 69 parts (0 on the bottom side), 22 nets.

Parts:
C1, C2, C11, C12, C15, C16, C17, C18: 100n; C_0603_1608Metric
C3, C4: 10u; C_1210_3225Metric
C5, C6: 22u; C_1210_3225Metric
C7, C8, C9, C10, C13, C14: 5p; C_0603_1608Metric
D1, D2, D3, D4: 1N4148; D_SOD-123
D5, D6: LED; LED_0603_1608Metric
H1, H2: MountingHole_Pad; MountingHole_2.7mm_M2.5_Pad
J1: Conn_01x03_Male; FanPinHeader_1x03_P2.54mm_Vertical
J2, J3: Conn_01x05_Male; PinHeader_1x05_P2.54mm_Vertical
J4, J5, J6: Conn_Coaxial; SMA_Molex_73251-2120_EdgeMount
R1, R4: 240; R_1210_3225Metric
R2, R3: 2.2k; R_1210_3225Metric
R5: 510; R_1210_3225Metric
R6, R7, R8, R9, R10, R12, R13, R14, R15, R16, R17, R18, R19, R20, R21, R22, R24: 10k; R_0603_1608Metric
R11: 470; R_1210_3225Metric
R23: 2k; R_0603_1608Metric
TP1: +12V; TestPoint_Pad_D1.0mm
TP2: -12V; TestPoint_Pad_D1.0mm
TP3: GND; TestPoint_Pad_D1.0mm
TP4: DIFFX-; TestPoint_Pad_D1.0mm
TP5: DIFFX+; TestPoint_Pad_D1.0mm
TP7: DIFFY-; TestPoint_Pad_D1.0mm
TP8: SUM-; TestPoint_Pad_D1.0mm
TP9: SUM+; TestPoint_Pad_D1.0mm
U1: LM317; SOT-223-3_TabPin2
U2: LM337; SOT-223-3_TabPin2
U3, U4, U5: OPA197xD; SOIC-8_3.9x4.9mm_P1.27mm

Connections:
+12V: C5.1, C11.2, C15.2, C17.2, D1.2, D3.1, D5.2, J2.1, R1.1, TP1.1, U1.2, U3.7, U4.7, U5.7
+15V: C1.1, D1.1, J1.1, U1.3
-12V: C6.2, C12.2, C16.2, C18.2, D2.1, D4.2, D6.1, J3.1, R4.2, TP2.1, U2.3, U3.4, U4.4, U5.4
-15V: C2.2, D2.2, J1.3, U2.2
/-X1: J2.4, R8.2, R13.2, R19.2
/-X2: J3.3, R6.2, R10.2, R20.2
/-Y1: J3.4, R7.2, R14.2, R21.2
/-Y2: J2.3, R9.2, R12.2, R22.2
/DIFFX: C7.1, J4.1, R17.1, U3.6
/DIFFY: C8.1, J5.1, R18.1, U4.6
/SUM: C13.1, J6.1, R24.1, U5.6
GND: C1.2, C2.1, C3.2, C4.1, C5.2, C6.1, C9.1, C10.1, C11.1, C12.1, C14.1, C15.1, C16.1, C17.1, C18.1, H1.1, H2.1, J1.2, J2.2, J2.5, J3.2, J3.5, J4.2, J5.2, J6.2, R2.2, R3.1, R5.2, R11.2, R15.1, R16.1, R23.1, TP3.1
unnamed: C3.1, D3.2, R1.2, R2.1, U1.1
unnamed: C4.2, D4.1, R3.2, R4.1, U2.1
unnamed: C7.2, R6.1, R7.1, R17.2, TP4.1, U3.2
unnamed: C8.2, R10.1, R12.1, R18.2, TP7.1, U4.2
unnamed: C9.2, R8.1, R9.1, R15.2, TP5.1, U3.3
unnamed: C10.2, R13.1, R14.1, R16.2, U4.3
unnamed: C13.2, R19.1, R20.1, R21.1, R22.1, R24.2, TP8.1, U5.2
unnamed: C14.2, R23.2, TP9.1, U5.3
unnamed: D5.1, R5.1
unnamed: D6.2, R11.1

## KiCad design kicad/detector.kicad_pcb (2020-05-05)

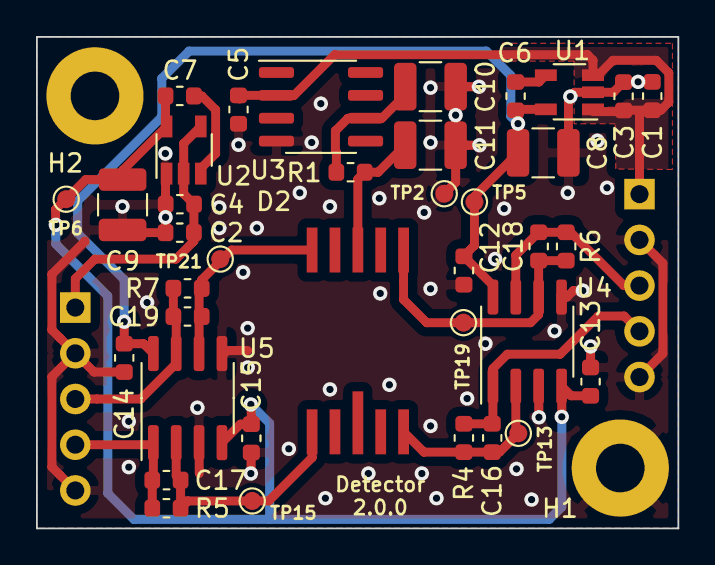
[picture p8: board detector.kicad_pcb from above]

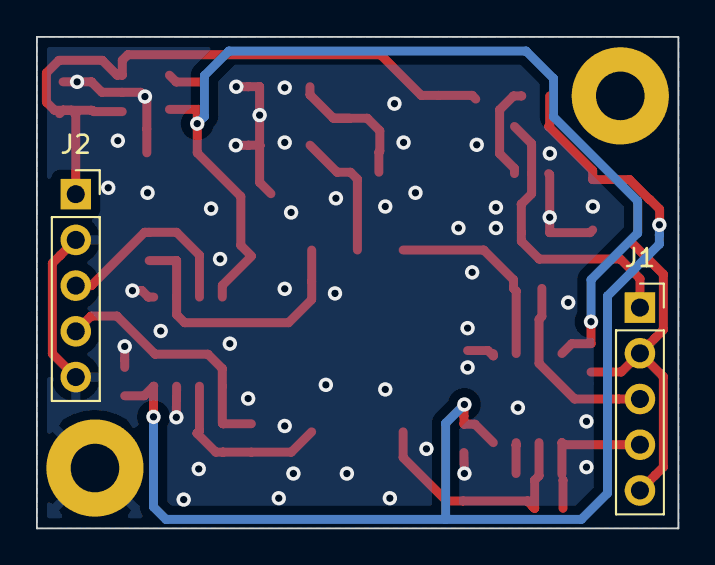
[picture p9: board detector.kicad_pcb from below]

Board: 2 copper layers, 35.6 x 27.3 mm, 41 parts (2 on the bottom side), 17 nets.

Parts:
C1, C2, C12, C13, C14, C15: 100n; C_0603_1608Metric
C3, C4, C5: 1u; C_0603_1608Metric
C6, C7: 10n; C_0603_1608Metric
C8, C9, C11: 22u; C_1210_3225Metric
C10: 10u; C_1210_3225Metric
C16, C17, C18, C19: 18p; C_0603_1608Metric
D2: S599x; S5990
H1, H2: MountingHole_Pad; MountingHole_2.7mm_M2.5_Pad
J1, J2: Conn_01x05_Male; PinSocket_1x05_P2.54mm_Vertical
R1: 100; R_0603_1608Metric
R4, R5, R6, R7: 6.04k; R_0603_1608Metric
TP2: GND; TestPoint_Pad_D1.0mm
TP5: +5V; TestPoint_Pad_D1.0mm
TP6: -5V; TestPoint_Pad_D1.0mm
TP13: I1; TestPoint_Pad_D1.0mm
TP15: I3; TestPoint_Pad_D1.0mm
TP19: I4; TestPoint_Pad_D1.0mm
TP21: I2; TestPoint_Pad_D1.0mm
U1: LT1761-5; TSOT-23-5
U2: LT1964-5; TSOT-23-5
U3: REF5010ID; SOIC-8_3.9x4.9mm_P1.27mm
U4, U5: OPA2197xD; SOIC-8_3.9x4.9mm_P1.27mm

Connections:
+5V: C6.2, C8.1, C12.2, C14.2, TP5.1, U1.5, U4.8, U5.8
+12V: C1.1, C3.1, C5.1, J2.1, U1.1, U1.3, U3.2
-5V: C7.1, C9.2, C13.2, C15.2, TP6.1, U2.5, U4.4, U5.4
-12V: C2.2, C4.2, J1.1, U2.2, U2.4
/-X1: C16.1, J2.4, R4.1, U4.1
/-X2: C19.1, J1.3, R7.1, U5.7
/-Y1: C17.1, J1.4, R5.1, U5.1
/-Y2: C18.1, J2.3, R6.1, U4.7
GND: C1.2, C2.1, C3.2, C4.1, C5.2, C8.2, C9.1, C10.2, C11.2, C12.1, C13.1, C14.1, C15.1, H1.1, J1.2, J1.5, J2.2, J2.5, TP2.1, U1.2, U2.1, U3.4, U4.3, U4.5, U5.3, U5.5
unnamed: C6.1, U1.4
unnamed: C7.2, U2.3
unnamed: C10.1, R1.2, U3.6
unnamed: C11.1, D2.8, R1.1
unnamed: C16.2, D2.1, R4.2, TP13.1, U4.2
unnamed: C17.2, D2.5, R5.2, TP15.1, U5.2
unnamed: C18.2, D2.10, R6.2, TP19.1, U4.6
unnamed: C19.2, D2.6, R7.2, TP21.1, U5.6

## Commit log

2019-02-19 started schematic of amplifier
    [Amplifier.kicad_pcb, Amplifier.sch]
2019-02-19 completed difference and summation stages
    [Amplifier.sch]
2019-02-19 redesigned blocks for space efficiency
    [Amplifier.sch]
2019-02-23 added LTSpice simulation files
    [Amplifier.kicad_pcb, Amplifier.sch]
2019-02-26 rewrote schematics
    [Amplifier.sch, Development.kicad_pcb, Development.sch]
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2019-03-04 renamed Photodiode kicad library to Library
    [Development.kicad_pcb, Development.sch]
2019-03-05 added voltage regulator to schematic
    [Development.sch]
2019-03-05 redesigned psd + preamp block in schematic
    [Development.sch]
2019-03-09 added optional offset compensation to preamplifiers
    [Development.sch]
2019-03-09 updated schematic title, company
    [Development.sch]
2019-03-09 added partial summing difference amplifier
    [Development.sch]
2019-03-09 added total summing amplifier
    [Development.sch]
2019-03-09 added test points to circuit
    [Development.sch]
2019-03-20 removed offset compensation, added bias voltage to schematic
    [Development.sch]
2019-03-20 updated schematics
    [Development.sch]
2019-03-20 extended circuit sheet size to A3, added connectors
    [Development.sch]
2019-03-21 replaced lemo with 3pin connector, created linear arthimetic amplifier section
    [Development.sch]
2019-03-21 added analog divider and connectors
    [Development.sch]
2019-03-21 renamed X,Y to POSX, POSY
    [Development.sch]
2019-03-21 replaced reverse bias voltage regulator with voltage reference
    [Development.sch]
2019-03-21 redrew schematic for improved readability, fixed output buffers
    [Development.sch]
2019-03-22 redrew schematic with kicad 5.1 without corrupted library
    [Development.sch, devel.kicad_pcb, devel.sch]
2019-03-22 converted schematic to flat hierarchical
    [arthimetic.sch, detector.sch, devel.sch, output.sch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]
2019-03-22 separated symbol library according to functionality
    [arthimetic.sch, detector.sch]
2019-03-22 redesigned S599x symbol according to symbol guidelines
    [detector.sch]
2019-03-22 redesigned AD538 symbol according to guidelines
    [arthimetic.sch]
2019-03-22 fixed opamp supply voltage polarisation, fixed output buffers
    [arthimetic.sch, detector.sch, output.sch]
2019-03-22 fixed floating buffer in arthimetic unit
    [arthimetic.sch, detector.sch, output.sch, power.sch]
2019-03-27 fixed arithmetic typo, decoupling cap polarisation
    [arithmetic.sch, detector.sch, devel.sch, output.sch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]
2019-03-27 removed arithmetic unit from development board, changed output connectors
    [detector.sch, devel.sch, output.sch, power.sch]
2019-03-27 made small adjustments, created netlist
    [detector.sch, output.sch, power.sch]
2019-03-27 removed inverting output opamps
    [output.sch]
2019-03-27 assigned footprints to symbols
    [detector.sch, output.sch, power.sch]
2019-03-27 created S5990 footprint, created pcb layout
    [detector.sch, devel.kicad_pcb]
2019-03-28 merged circuit sheets to single sheet, removed extra diodes, changed diode type
    [devel.kicad_pcb, devel.sch, output.sch, power.sch]
2019-03-28 reassigned footprints that were not smd compatible
    [devel.kicad_pcb, devel.sch]
2019-03-28 created first pcb layout draft
    [devel.kicad_pcb, devel.sch]
2019-03-29 simplified circuit schematic, used uniform resistor footprints
    [devel.kicad_pcb, devel.sch]
2019-03-29 completed sublayout of detector and preamp
    [devel.kicad_pcb, devel.sch]
2019-03-29 completed sublayout of bias voltage reference
    [devel.kicad_pcb, devel.sch]
2019-03-29 added mosfet polarity protection to power connector
    [devel.sch]
2019-03-29 added protection diodes to supply voltage regulators
    [devel.sch]
2019-03-29 fixed details in power connector circuit
    [devel.sch]
2019-03-29 updated footprint assignment
    [devel.sch]
2019-03-29 changed diode circuit symbols to small, updated footprints
    [devel.sch]
2019-03-30 completed sublayout of power input
    [devel.kicad_pcb, devel.sch]
2019-03-30 completed pcb sublayouts
    [devel.kicad_pcb]
2019-03-30 retraced regulators according to datasheet layout
    [devel.kicad_pcb]
2019-03-30 moved sublayouts around
    [devel.kicad_pcb]
2019-04-01 created custom sma footprints
    [devel.kicad_pcb, devel.sch]
2019-04-01 completed pcb layout routing
    [devel.kicad_pcb, devel.sch]
2019-04-01 replaced sma connector footprint
    [devel.kicad_pcb, devel.sch]
2019-04-01 completed pcb layout with cooper fills
    [devel.kicad_pcb]
2019-04-02 updated pcb layout, added screws
    [devel.kicad_pcb, devel.sch]
2019-04-02 improved cooper fill zones
    [devel.kicad_pcb]
2019-04-03 realigned vias, added silk labels
    [devel.kicad_pcb, devel.sch]
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2019-04-25 removed notebooks, updated folder structure
    [arithmetic.sch, arthimetic.sch, detector.sch, devel.kicad_pcb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]
2019-04-25 removed old scheets, updated symbol paths
    [arithmetic.sch, arthimetic.sch, detector.sch, devel.kicad_pcb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]
2019-04-30 started modular PCB design
    [arithmetic.sch, detector.sch, devel.sch, power.sch]
2019-07-30 created modular project with schematic and shield component
    [detector.sch, modular.kicad_pcb, modular.sch, power.sch]
2019-07-30 removed signal shield from power module, updated page settings
    [detector.sch, modular.sch, power.sch]
2019-07-30 added more test points to modular, assigned some footprints
    [detector.sch, power.sch]
2019-07-31 completed header footprint, started with pcb design of power board
    [detector.sch, power.sch]
2019-07-31 completed pcb design of power board
    [modular.kicad_pcb]
2019-07-31 updated detector board footprints, added edge cuts
    [modular.kicad_pcb]
2019-08-01 completed detector board
    [detector.sch, modular.kicad_pcb]
2019-08-01 started redesign of pcb
    [detector.sch, modular.kicad_pcb, power.sch]
2019-08-01 redesigned pcb with more symmetry
    [detector.sch, modular.kicad_pcb]
2019-08-02 applied pcb design suggestions to modular boards
    [detector.sch, modular.kicad_pcb, power.sch]
2019-08-02 removed overlap of component labels in modular boards
    [modular.kicad_pcb]
2019-08-02 fixed opamp input terminal connection, connected some caps directly to gnd through vias
    [detector.sch, modular.kicad_pcb]
2019-08-02 added keepout area for copper fill under opamp
    [modular.kicad_pcb]
2019-08-05 via stitched gnd trace of voltage reference, added zones around voltage regulators
    [modular.kicad_pcb]
2019-08-10 added arithmetic board to modular design
    [arithmetic.sch, detector.sch, modular.sch, power.sch]
2019-08-14 completed schematic of arthimetic board
    [arithmetic.sch]
2019-08-23 added pcb design of arithmetic board
    [arithmetic.sch, modular.kicad_pcb]
2019-08-23 updated arithmetic schematic with resistor arrays and dual opamp, removed old footprints
    [arithmetic.sch, modular.kicad_pcb]
2019-08-23 applied pcb design feedback to arithmetic board
    [arithmetic.sch, modular.kicad_pcb]
2019-08-23 created experimental project
    [adc-current.sch, adc-voltage.sch, buffer.sch, ethernet.sch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]
2019-08-25 removed current adc components from experimental kicad design
    [adc-current.sch, adc-voltage.sch, adc.sch, buffer.sch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]
2019-08-25 created schematic for experimental adc
    [adc.sch, buffer.sch]
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2019-09-25 fixed generic opamp symbol pin layout, updated pcb of arithmetic board
    [arithmetic.sch, modular.kicad_pcb]
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2020-03-19 replaced OPAx197s with standard library symbols, increased voltage regulator caps
    [arithmetic.sch, detector.sch]
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2020-03-20 replaced voltage regulators of 2.0.0 detector with LDO regulators
    Low-dropout (LDO) voltage regulators come in small packages, i.e.
    SOT-23, however they are more susceptible for ringing.
    The packages in which you can buy the non-LDO voltage regulators, e.g. SOIC-8 or SOT-223,
    are large compared to the remaining circuitry.
    [detector.kicad_pcb, detector.sch]
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2020-04-13 replaced dual op-amp on 2.0.0 arithmetic board with two op-amps
    [arithmetic.kicad_pcb, arithmetic.sch]
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2020-04-17 completed redesign of arithmetic and detector 2.0.0 boards
    [arithmetic.kicad_pcb, detector.kicad_pcb]
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2020-04-20 fixed signal routing, remaining vias, large traces
    [arithmetic.kicad_pcb]
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2020-04-24 added mounting holes to eeschema, replaced mounting holes with pad
    [arithmetic.kicad_pcb, arithmetic.sch, detector.kicad_pcb, detector.sch]
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2020-04-25 redesigned detector pcb
    [detector.kicad_pcb, detector.sch]
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2020-05-05 fix some DRC errors, remove some test points
    [arithmetic.kicad_pcb, detector.kicad_pcb, detector.sch]
2020-05-13 applied suggestions from Bodo Hecker
    * changed R23 to 2k
    * replaced pin holes in detector with padded pin holes
    * increased casing of led resistors to 1210
    [arithmetic.kicad_pcb, arithmetic.sch]
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2020-10-07 replaced measurements, updated analysis notebook
    [bottom.csv, center-left.csv, center-right.csv, center.csv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]
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
